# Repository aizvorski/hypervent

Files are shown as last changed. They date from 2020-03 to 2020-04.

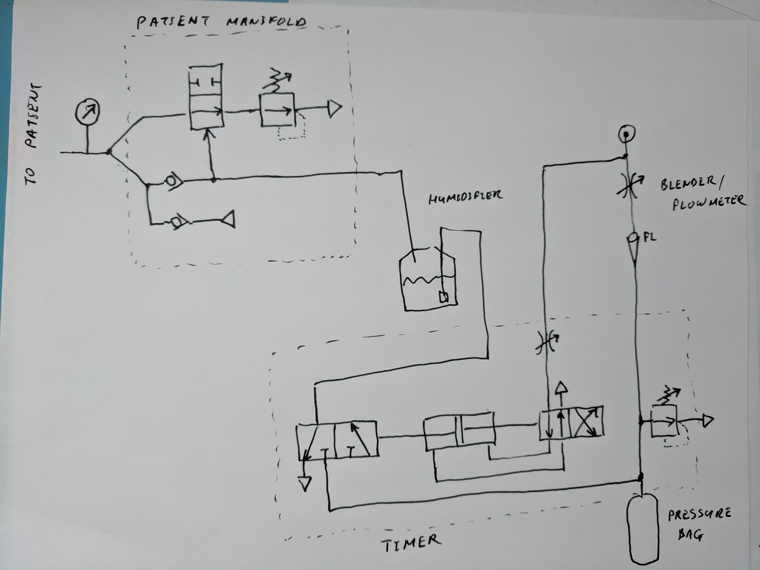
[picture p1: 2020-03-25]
Chua_system_diagram.jpg

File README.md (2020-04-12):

## COPYRIGHT AND LICENSE

Copyright 2020 Alex Izvorski <aizvorski@gmail.com>

This Source (CAD files and other design materials) describes Open Hardware and is licensed under the CERN-OHL-S v2.

You may redistribute and modify this Source and make products using it under the terms of the CERN-OHL-S v2 (https:/cern.ch/cern-ohl).

This documentation is distributed WITHOUT ANY EXPRESS OR IMPLIED WARRANTY, INCLUDING OF MERCHANTABILITY, SATISFACTORY QUALITY AND FITNESS FOR A PARTICULAR PURPOSE. Please see the CERN-OHL-S v2 for applicable conditions.

Source Location: https://github.com/aizvorski/hypervent

As per CERN-OHL-S v2 section 4, should You produce hardware based on this Source, You must maintain the Source Location visible on the external case of the hardware or other product you make using this Source.

## DISCLAIMER OF WARRANTY, EXCLUSION AND LIMITATION OF LIABILITY

Additionally, the following important disclaimers from the CERN-OHL-S v2 license apply to all use (reproduced below for clarity).  Do not download or use these files unless you have read and agree with the following.

  6.1 DISCLAIMER OF WARRANTY -- The Covered Source and any Products
      are provided 'as is' and any express or implied warranties,
      including, but not limited to, implied warranties of
      merchantability, of satisfactory quality, non-infringement of
      third party rights, and fitness for a particular purpose or use
      are disclaimed in respect of any Source or Product to the
      maximum extent permitted by law. The Licensor makes no
      representation that any Source or Product does not or will not
      infringe any patent, copyright, trade secret or other
      proprietary right. The entire risk as to the use, quality, and
      performance of any Source or Product shall be with You and not
      the Licensor. This disclaimer of warranty is an essential part
      of this Licence and a condition for the grant of any rights
      granted under this Licence.

  6.2 EXCLUSION AND LIMITATION OF LIABILITY -- The Licensor shall, to
      the maximum extent permitted by law, have no liability for
      direct, indirect, special, incidental, consequential, exemplary,
      punitive or other damages of any character including, without
      limitation, procurement of substitute goods or services, loss of
      use, data or profits, or business interruption, however caused
      and on any theory of contract, warranty, tort (including
      negligence), product liability or otherwise, arising in any way
      in relation to the Covered Source, modified Covered Source
      and/or the Making or Conveyance of a Product, even if advised of
      the possibility of such damages, and You shall hold the
      Licensor(s) free and harmless from any liability, costs,
      damages, fees and expenses, including claims by third parties,
      in relation to such use.

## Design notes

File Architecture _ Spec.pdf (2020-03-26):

System diagram

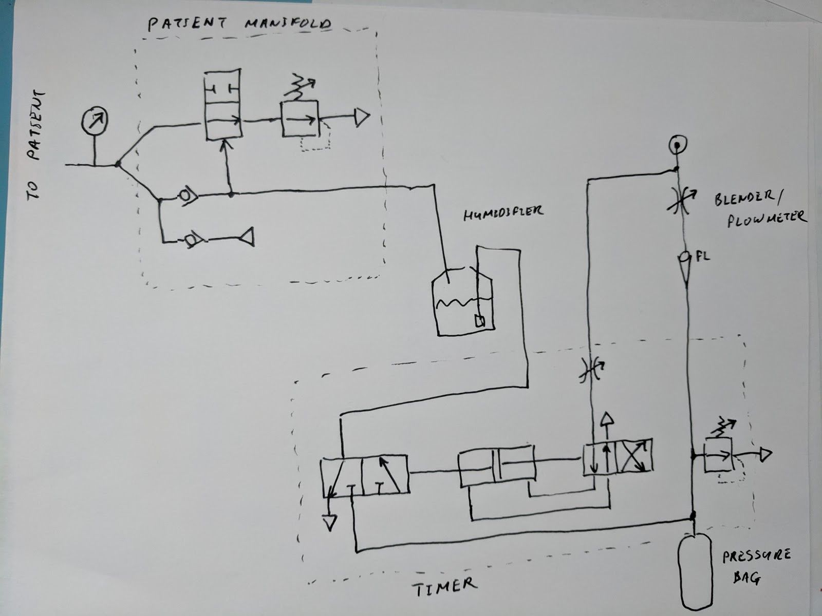
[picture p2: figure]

Operating principle

A constant flow of oxygen or oxygen/air mix from the source (controlled by blender or needle valve) sets the minute volume. Pressure in the bag increases until outflow matches inflow; in other words the PIP pressure is at the lowest pressure that allows the set minute volume (=Pressure Regulated Volume Control mode). The minute volume does not depend on lung compliance.

If the pressure builds up too high, the PIP overpressure valve vents excess pressure from the bag (and sounds an alarm whistle)

The pneumatic timer is driven by a separate oxygen flow at higher pressure but lower volume, about 0.15-0.2 lpm at 10 psi. The timer consists of a double acting cylinder and two piston valves in one body (~4 parts total). At each position of the piston, the valve is set to gradually feed pressure to that side until the piston is released and flips to the opposite side. This requires a means to hold the piston in place until a set force threshold; this may be implemented as a spring loaded catch, a bistable spring (stamped metal), friction, or (preferably) a magnet at each end of the cylinder.

The cycle time of the timer is set by time needed to reach the force/pressure needed to release the piston at the flow rate coming from the needle valve. The time can be unequal for the two sides, based on either a different holding force, or a different dead volume. The cycle time does not depend on lung compliance, PIP or minute volume.

During inspiration, the bag pressure acts to close the output valve in the patient manifold. The valve can be realized as a duck billed valve or a piston and spring valve. The same valve can control the PEEP (~4 parts)

Timer

See "Timer" doc for detailed description

cycle time 10-30 cycles per second
on time : off time ratio 1:2 (can be fixed or adjustable - change the volume on one side of the cylinder or the magnet standoff)
driven from 3.5-4.5 bar supply
should not use more than 0.2lpm

Timer pressure relief valve

fixed 35 cmH2O
(option) adjustable 35 cmH2O-70 cmH2O must allow >10lpm at 40cmH2O

Patient manifold valve

closes at 10 cmH2O or greater
must remain closed with pressure differential up to 35cm H2O between input and output full port: 100mm^2 (pref 300mm^2)

Patient manifold pressure relief valve (PEEP valve)

adjustable 5 to 20 cmH2O

Blender

standard equipment http://www.biomeddevices.com/products/categories/low-flow-air/oxygen-blenders-for-the-nicu-and-l-d/ (http://www.biomeddevices.com/products/categories/low-flow-air/oxygen-blenders-for-the-nicu-and-l-d/)

Can use a needle valve (injection molded) and/or venturi (injection molded). It is expected that in an emergency everyone will be on 100% oxygen.

Can also use oxygen concentrator (preferably two, connected with a Y)

Flowmeter

standard equipment

https://mfimedical.com/products/allied-healthcare-timeter-sure-grip-single-oxygen-flowmeter

If unavailable: can use injection molded rotameter (2 parts)

Pressure monitor

standard equipment - disposable pressure gauge from Mercury Medical
(6 components including one spring, rest is injection molded)

If unavailable: can make a clone from injection molded components, or use a U tube manometer, or connect a gauge to check pressure once in a while

Pressure bag

Anaesthesia bag, 3 liter (standard equipment)

https://serfinitymedical.com/products/portex-anesthesia-breathing-circuit-expandable-tube-87-in ch-tube-dual-limb-adult-3-liter-bag-disposable-smiths-medical-453600-nl-653642 (https://serfinitymedical.com/products/portex-anesthesia-breathing-circuit-expandable-tube-87-inch-tube-dual-limb-adult-3-liter-bag-disposable-smiths-medical-4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)

Specs are not critical; can use any elastic bag several liters in size and rated to 2-3 psi.

If unavailable: can use a soda bottle; elasticity is preferred but not absolutely required, the main function is of a pressure accumulator.

Flutter valves (check valves)

standard equipment:
https://www.respiratorycarestore.com/carefusion-001802-airlife-one-way-flutter-valve-large-22m m-o-d (https://www.respiratorycarestore.com/carefusion-001802-airlife-one-way-flutter-valve-large-22mm-o-d)

If unavailable: can be made from injection molded body and die cut rubber sheet

Connectors

22mm ID/OD slip fit (standard) per ISO 5356-1

Tubing

standard equipment

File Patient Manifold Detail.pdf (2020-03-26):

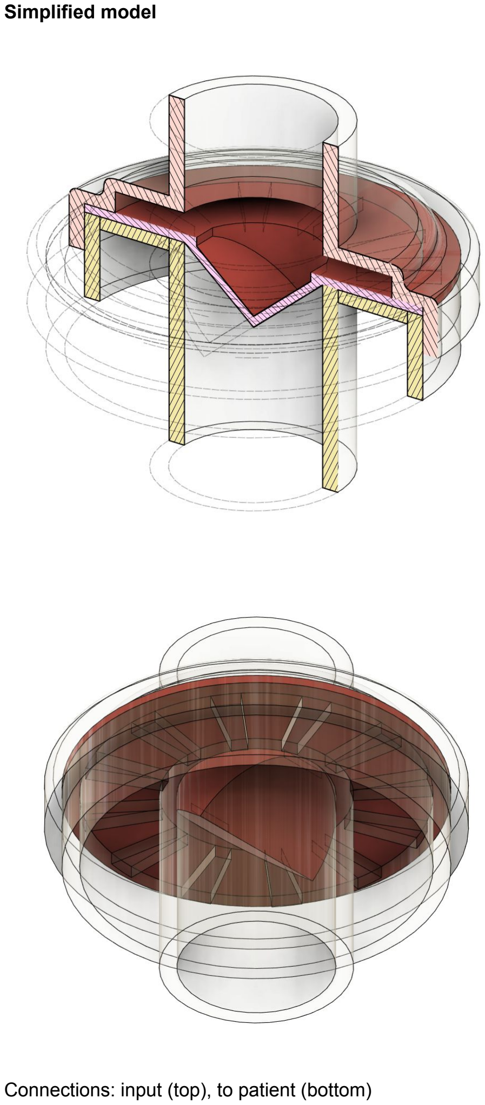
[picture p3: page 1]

Simplified model

Connections: input (top), to patient (bottom)

The patient manifold (as shown here) consists of a duck bill valve which (a) closes the exhalation port and allows inhalation when pressured from the input side, and (b) opens during exhale and controls PEEP due to its stiffness

An additional spring loaded adjustment can increase/decrease PEEP by providing additional pressure against the back of the diaphragm. Alternatively, different diaphragms can be used for different PEEP levels.

Not shown: anti-suffocation flutter valve; airway pressure manifold; PEEP adjustment

A piston and spring based version can also be used; it is likely to be a bit more complex

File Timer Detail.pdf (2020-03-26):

The timer consists of a double acting cylinder and two piston valves in one body (~4 parts total); and a needle valve to control the timing.

Other implementations are possible as long as they have the same bistable functionality. Diaphragm and rotary-type mechanisms were also considered; however the cylinder appears to have the lowest risk / highest likelihood of working on the first iteration.

Simplified model

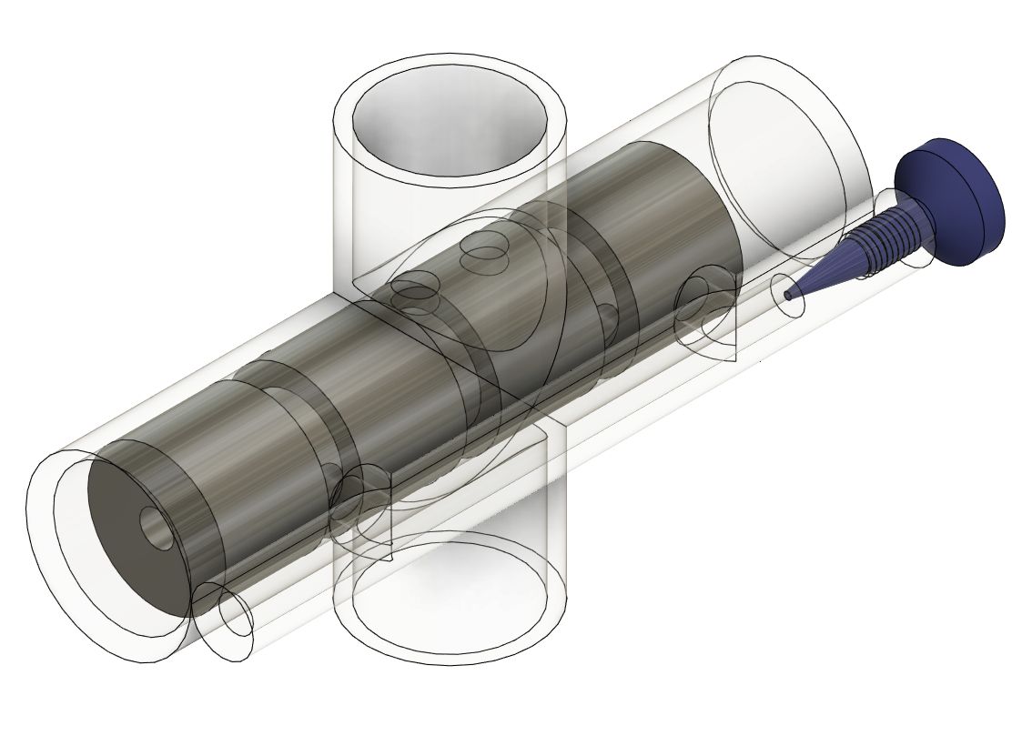
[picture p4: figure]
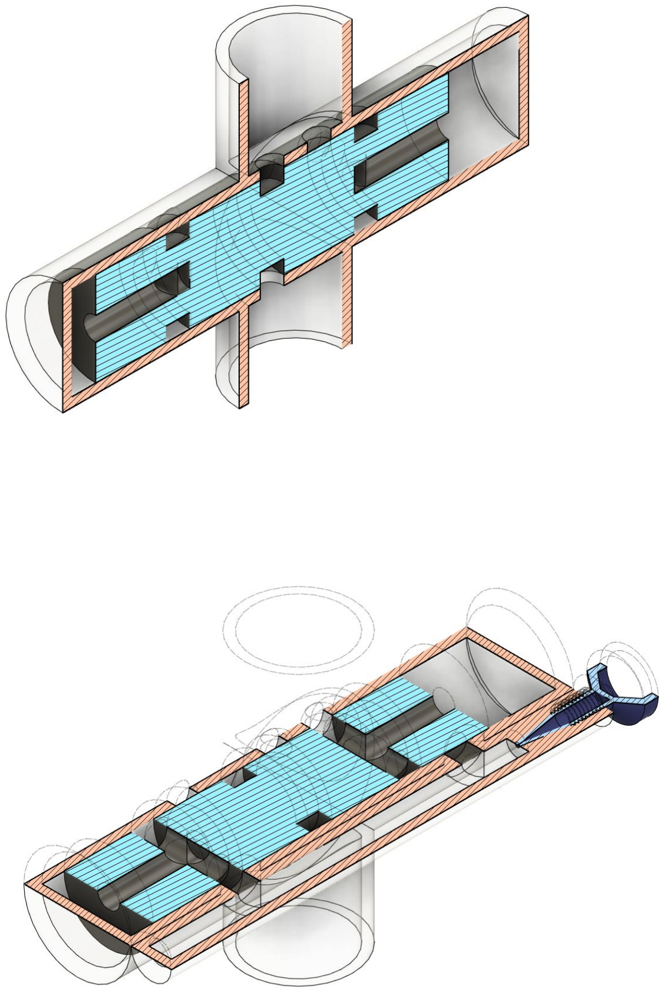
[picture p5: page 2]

Connections

Top - to patient manifold
Bottom - to pressure bag
Right (small port) - needle valve controlling cycling speed
(this is shown during inhale; during exhale the piston moves to the opposite side)

Not shown: overpressure relief; connection to O2 feed (these will be combined with another flow controller and rotameter)

How it works

In either piston position: pressure is building up through the needle valve at a controlled rate to flip it to the other position. The other side of it is open to the atmosphere so it won't create a force in the opposite direction

The piston needs some kind of retaining feature at each end - this could be a buckling spring with two positions, a catch, or magnets. Magnets are most likely to have a predictable and repeatable holding force

After the pressure builds above the holding force, the piston flips to the other side (quite fast), the pressure behind it vents to the atmosphere, and the cycle repeats in the opposite direction

Implementation notes

Steel piston; magnets at either end (preferred); or plastic piston with steel washers and magnets; or plastic piston with bistable spring (no magnets)

Plastic cylinder (polycarbonate or K resin, injection molded), or metal cylinder made from a piece of tubing, inside plastic cross piece (pressure fit)

Piston end-stops to control timing/holding force (and cushion)

Metal on metal would allow a closer fit - estimate 0.25mm clearance needed for plastic or 0.1mm free running fit for metal. Trade off is that plastic may either need O ring seals (silicone) or may have a relatively high leakage rate. The design would still operate correctly at leakage rates up to a few liters per minute; the timing valve would just need to be opened wider.

Operating parameters

Operating pressure 2-5 psi (pressure reserve up to 10 psi ensures cycling even if piston sticks) Flow 150 ml/minute (at 10 cycles/minute)
Holding force at each end 1-2 lbf (this should be significantly more than piston stiction)

Piston area ~3 cm^2
Open port 0.2 cm^2 (can be increased to about 0.5-1 cm^2 by changing port shape, or just scale up the cylinder/piston)

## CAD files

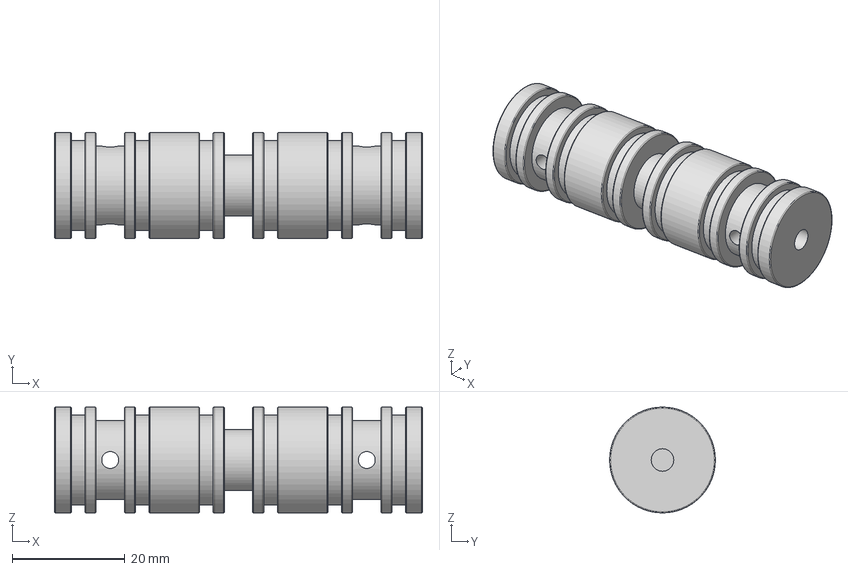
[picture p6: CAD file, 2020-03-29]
Timer ORings v3.step
65.3 x 18.8 x 18.8 mm

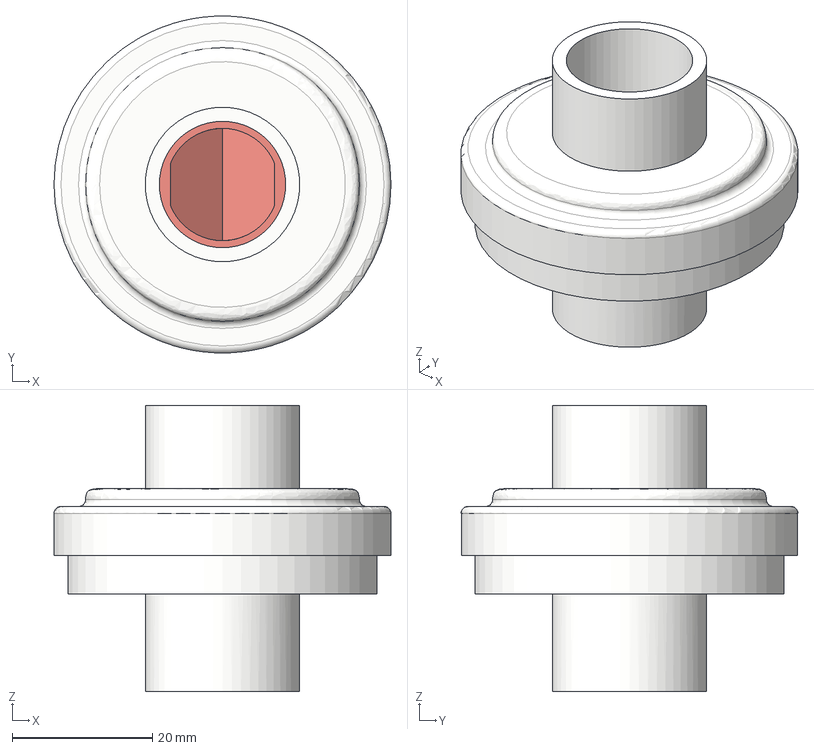
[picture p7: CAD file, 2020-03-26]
Patient Manifold v2.step
48.0 x 48.0 x 40.8 mm
Diaphragm
Top
Bottom

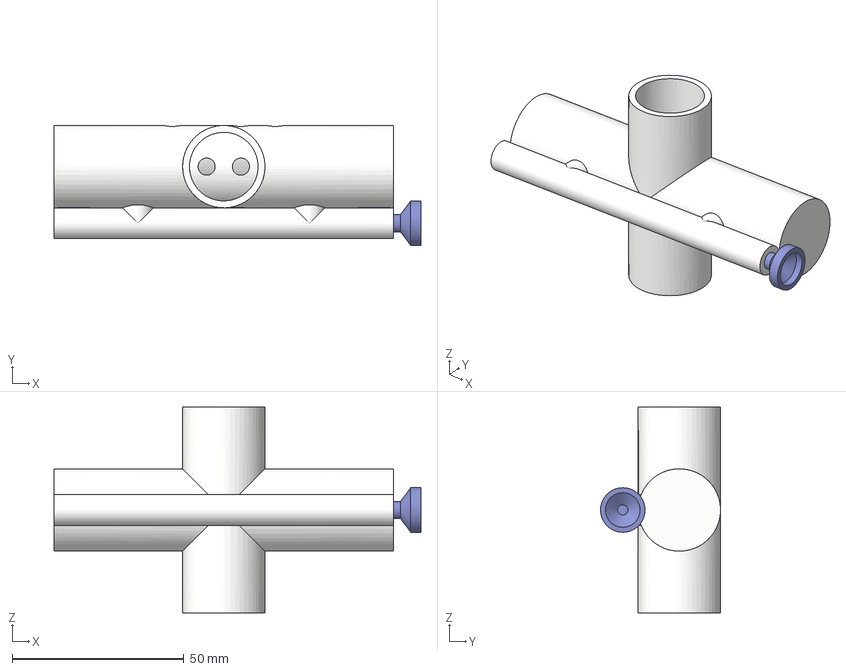
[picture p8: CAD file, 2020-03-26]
Timer v8.step
107.0 x 35.0 x 60.0 mm
Piston
Valve

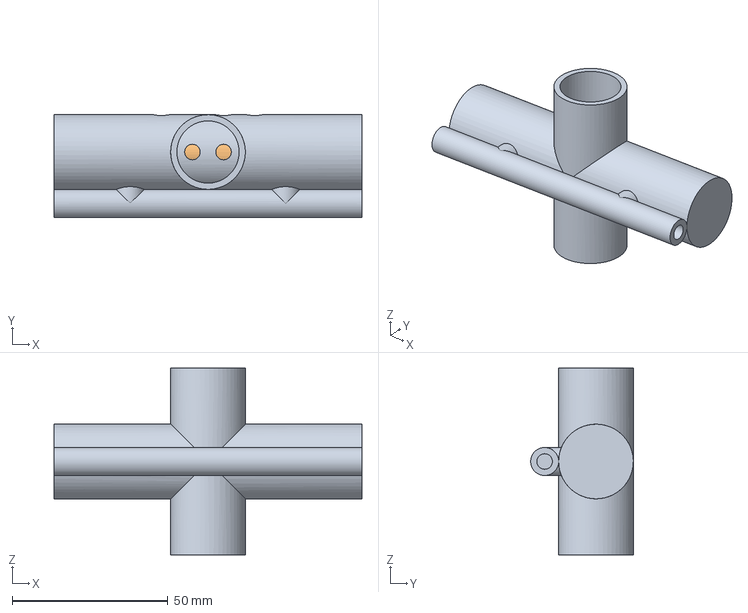
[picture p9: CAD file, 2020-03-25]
Timer v4.step
99.0 x 33.0 x 60.0 mm
Piston

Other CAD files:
Patient Manifold v2.f3d
Timer ORings v3.f3d
Timer v4.f3d
Timer v8.f3d

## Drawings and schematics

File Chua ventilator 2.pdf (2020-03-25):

# Chua ventilator 2

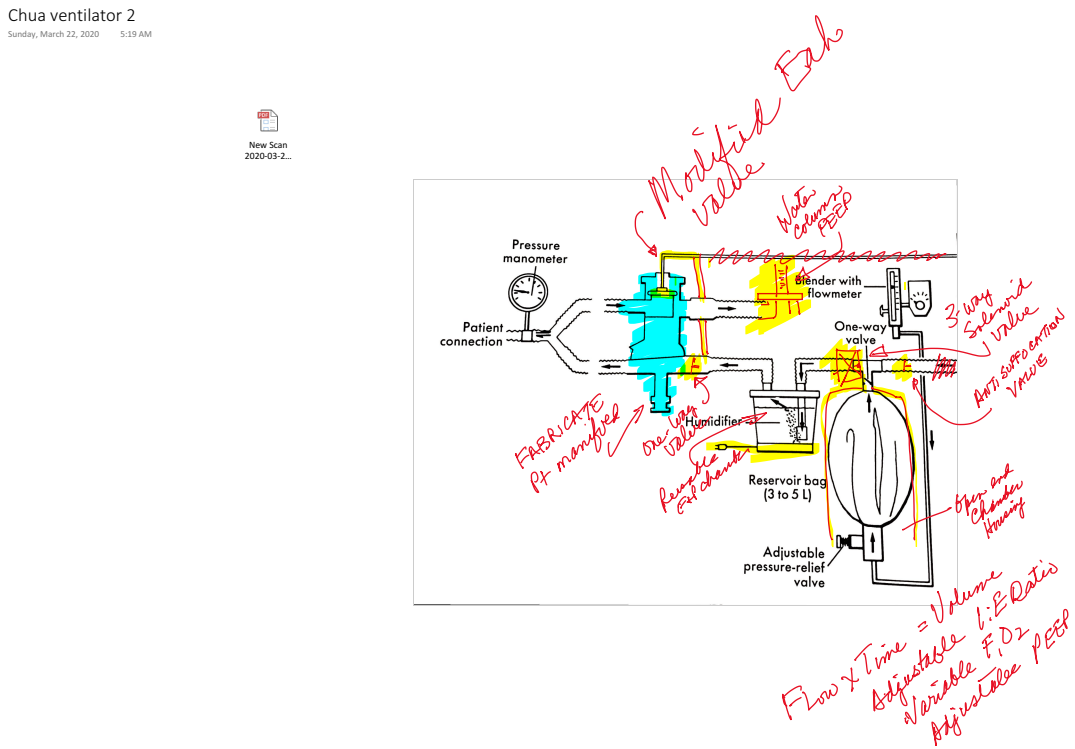
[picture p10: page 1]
New Scan 2020-03-2…; Sunday, March 22, 2020

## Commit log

2020-03-25 STEP files
    [Timer v4.step]
2020-03-26 Updated cad
    [Patient Manifold v2.f3d, Patient Manifold v2.step, Timer v8.f3d, Timer v8.step]
